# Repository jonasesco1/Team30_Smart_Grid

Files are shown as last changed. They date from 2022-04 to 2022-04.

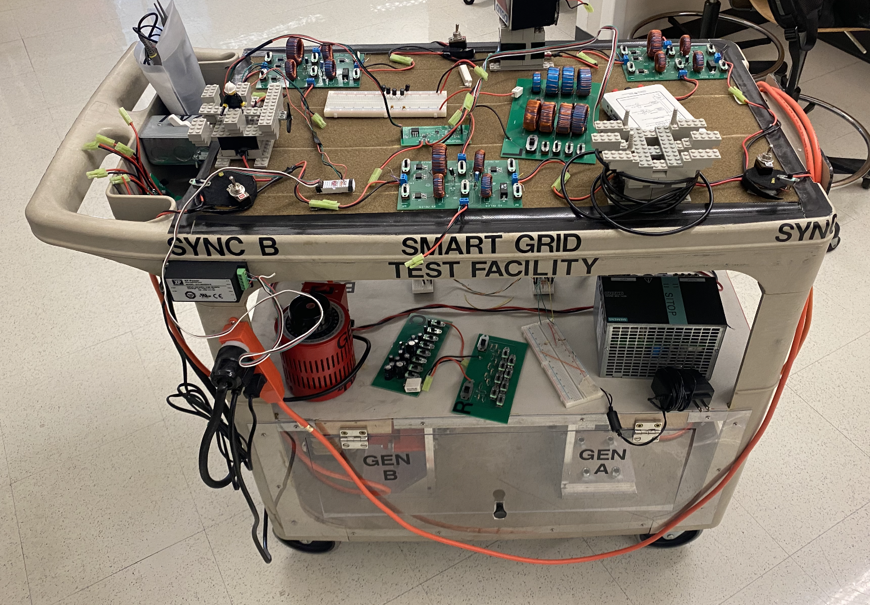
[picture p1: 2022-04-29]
2022 Team/Hardware Documentation/Pictures/Grid Side view.png

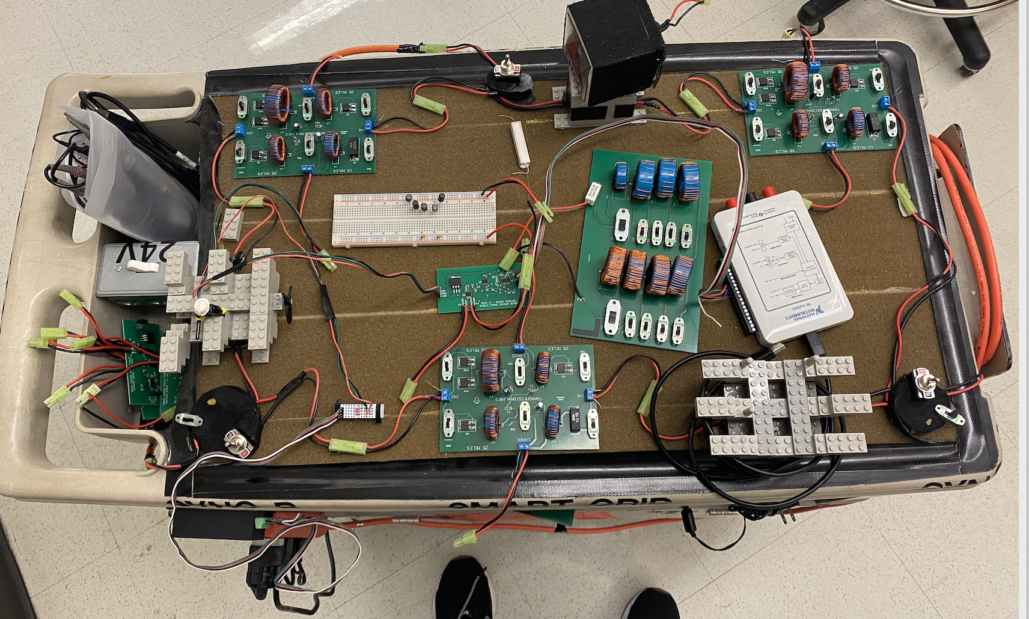
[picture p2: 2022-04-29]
Hardware Documentation/Pictures/Grid Sky View.png

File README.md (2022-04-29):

# Team30 Smart Grid

## The Team

The creators of this project are:

| Name  | Email |
| ------------- | ------------- |
| Jonas Escobar  | jesco@bu.edu  |
| Aidan McCall  | apm22@bu.edu  |

## The Client

The client of this project is Professor Alan Pisano (apisano@bu.edu). 

## The Purpose

The purpose of this project is to design a test facility that can be used by a professor to teach students about how an electrical grid works including generation, transmission, distribution, phasors, and loads. 

## How to use

This repository is meant to help inform a professor, student, or future design team how the test facility works and operates. Please note that there were two groups that worked on this project: Labeled as 2015 Team and 2022 Team. The 2015 Team did a majority of the design on the grid model, and the 2022 Team designed the data acquisition system. Most of the 2015 Team's work carried for over into into the 2022 Team. However, in the event of any differences, default to the 2022 Team. 

Both folders are set up the same way including software documentation, hardware documentation, pictures, and all reports completed throughout the semester. The 2022 hardware documentation and software documentation Readme's and 2022 User's Manual will be the most helpful in operating the test facility. 

### Hardware

Hardware can be split up into two different categories: data acquisition unit hardware and test facility hardware. The DAQ information is found in the 2022 Hardware documentation folder and includes information about the sensor boards, myDAQ, and PicoScope. The test facility hardware is found in the 2015 Hardware documentation folder and includes information about the generators, synchronization method, and transmission line boards. 

### Software

Most of the software documentation is found in the 2022 Software Documentation folder including all MATLAB code for the myDAQ and information on the PicoScope. Code for the MSP430 feedback boards is found in the 2015 Software Documentation folder.

### Reports

All reports for all teams are found the respective folders. The most important report is the User's Manual although the other reports highlight the engineering process each team went through. A user only needs to read the 2022 User's Manual in order to understand and operate the test facility. However, the 2015 User's Manual has good supplemental information in case of modifications or confusion.

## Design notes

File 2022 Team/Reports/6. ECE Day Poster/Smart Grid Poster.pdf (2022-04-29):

# Team 30: Smart Grid

Scale Energy Grid Model | Boston University ECE
Aidan McCall and Jonas Escobar
Background | Software

# Purpose

- The energy grid brings electric power to systems that need it: houses, businesses, manufacturing buildings, etc.
- The grid infrastructure is made up of generation, transmission, and distribution, and then consumption by the end use system
- An important function is to integrate multiple different generation sources into the same transmission grid

Educational Tool
- Create an educational tool that can be used by a professor to teach students about electrical grids by:
- Measuring voltage, current, phase angle, and power factor on a grid under different transmission and load configurations
- Verifying grid measurements using circuit principles learned in class
- Simulating blackouts
Updated Design
- Fix bugs associated with inherited grid model
- Add data acquisition system to enhance the already-functioning grid

Measure
Frequency

Adjust
Frequency

CONSUMPTION
(LOADS)

DATA READOUT

TRANSMISSION

GENERATION

DISTRIBUTION | Picoscope
- Live waveform data
- Verify stable grid
operation
- Synchronize generators

Special Thanks to:
- Power Pooches for designing the original grid model
- Professors Pisano, Osama and Hirsch for guidance and support

Connect hardware
- Connect data acquisition unit at the push of a button Frequency Analysis
- Graph current and voltage waveforms
- Provide frequency analysis to confirm 60 Hz

Visualization
- Graph current and voltage waveforms
- Plot Phasor Diagram to
visualize leading and
lagging power factor
- Provide RMS current, RMS voltage, phase angle, and
power factor data

FEEDBACK

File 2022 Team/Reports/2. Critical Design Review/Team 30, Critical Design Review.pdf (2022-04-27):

# Team 30: Smart Grid

By: Aidan McCall and Jonas Escobar

# Problem Statement

We have a fully functional Electric Grid model from a previous Senior Design

team that has no working method for data collection, so it cannot be properly

utilized by professors for classes like EC 417.

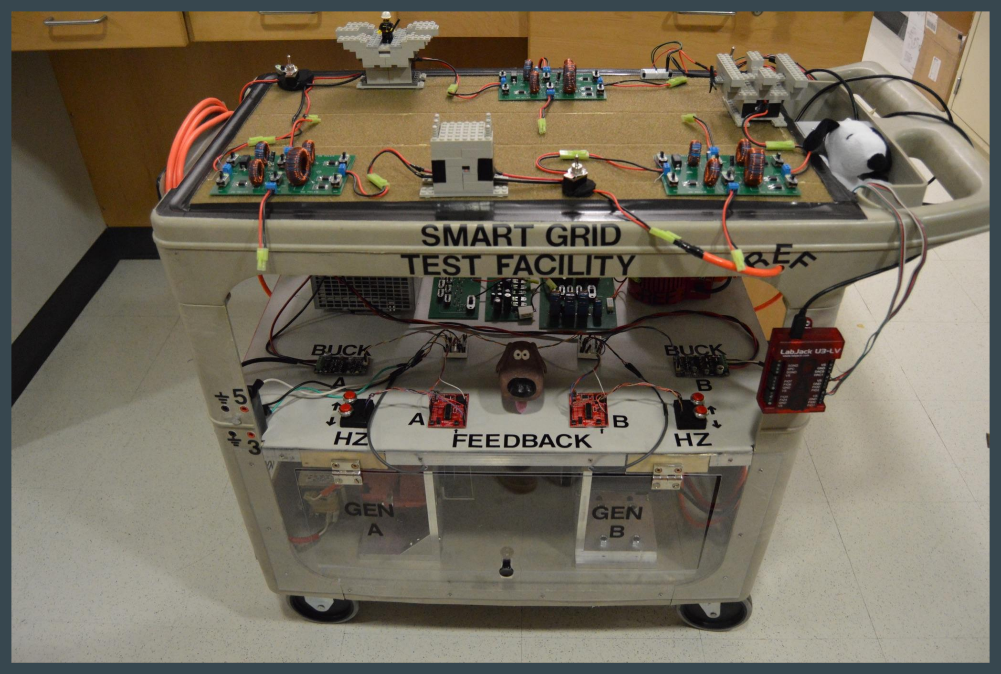
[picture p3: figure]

# The Smart Grid Model

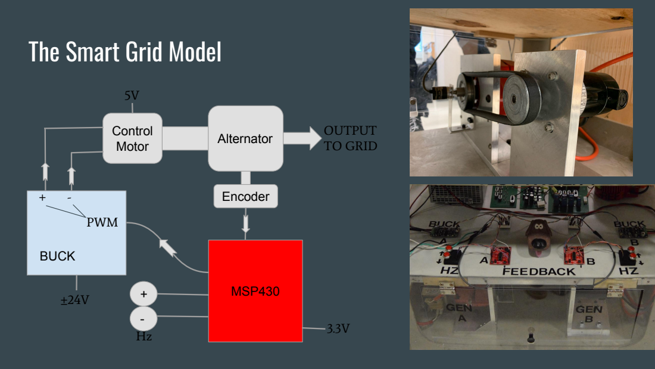
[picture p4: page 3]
MSP430; BUCK; PWM; Control; Motor; Alternator; Encoder; OUTPUT TO GRID

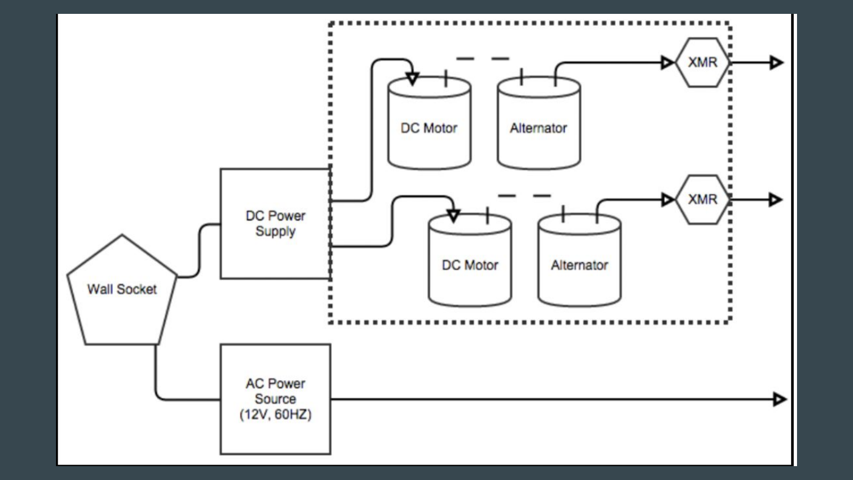
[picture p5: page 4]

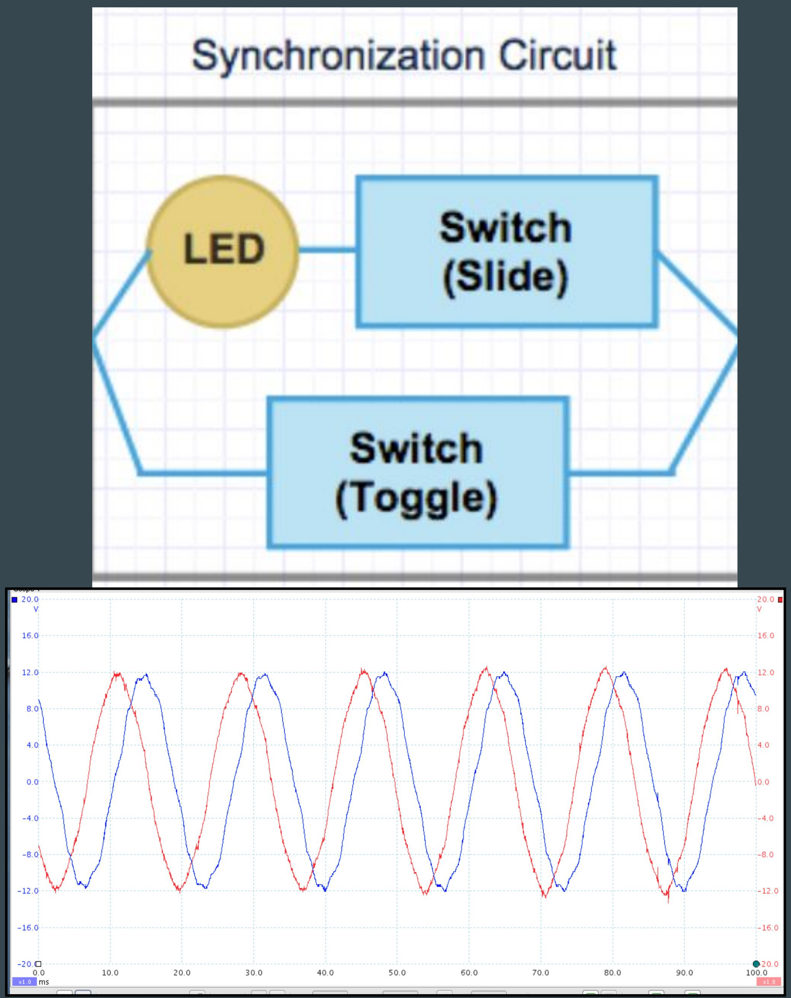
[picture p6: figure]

# Synchronization

- Synchronization
- "Sync Bulb" method
- Problem: LED can be hard to

time and a big oscilloscope

can practically be transported

- Solution: Picoscope

# Data Collection

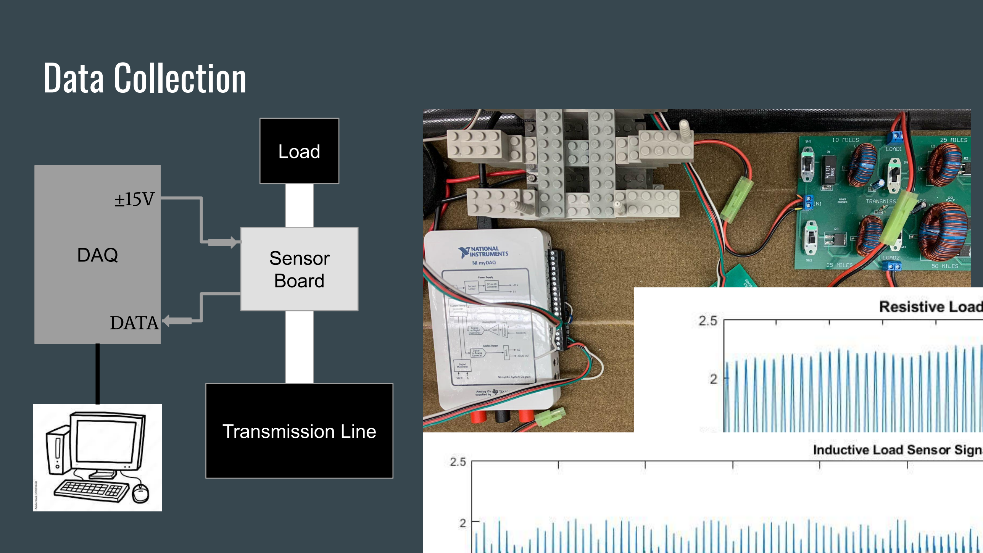
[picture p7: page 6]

Transmission Line

DAQ | Sensor Board Load

±15V

DATA

# GUI

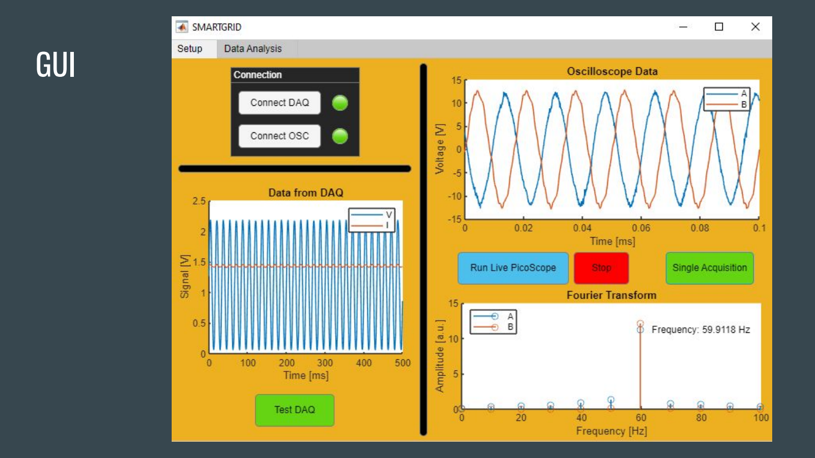
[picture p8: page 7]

# Next Steps

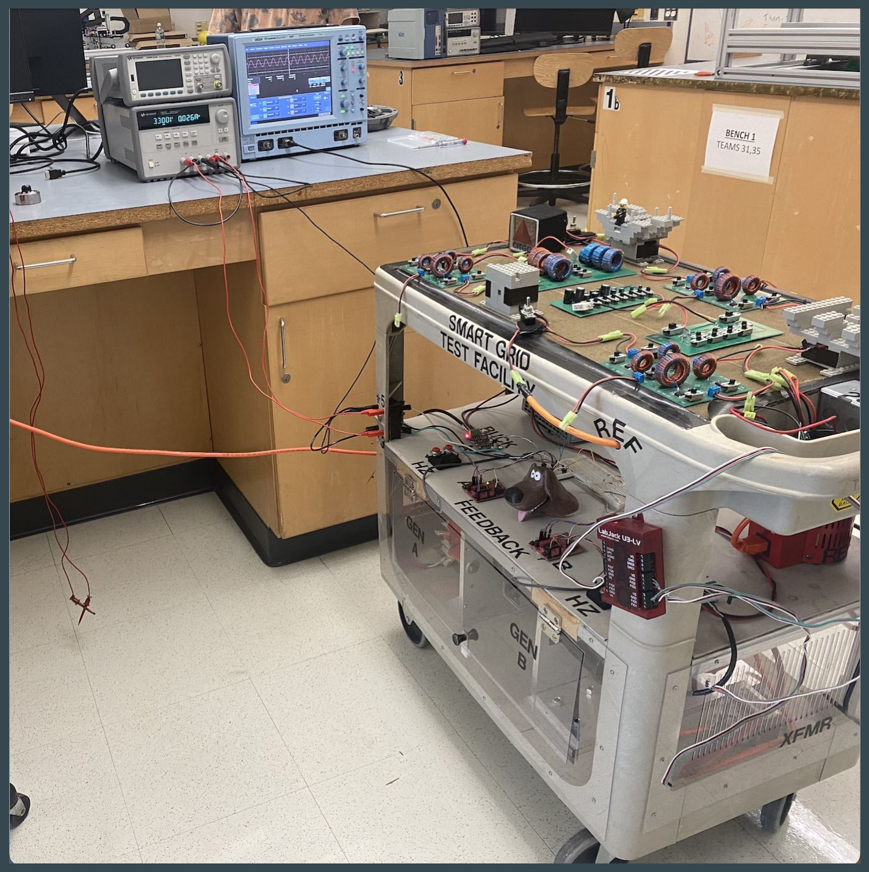
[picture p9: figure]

- Consolidate everything into one movable cart
- Use the DAQ
- Update our GUI and DAQ code to be able to calculate phasors (and therefore power factor)

# Gantt Chart

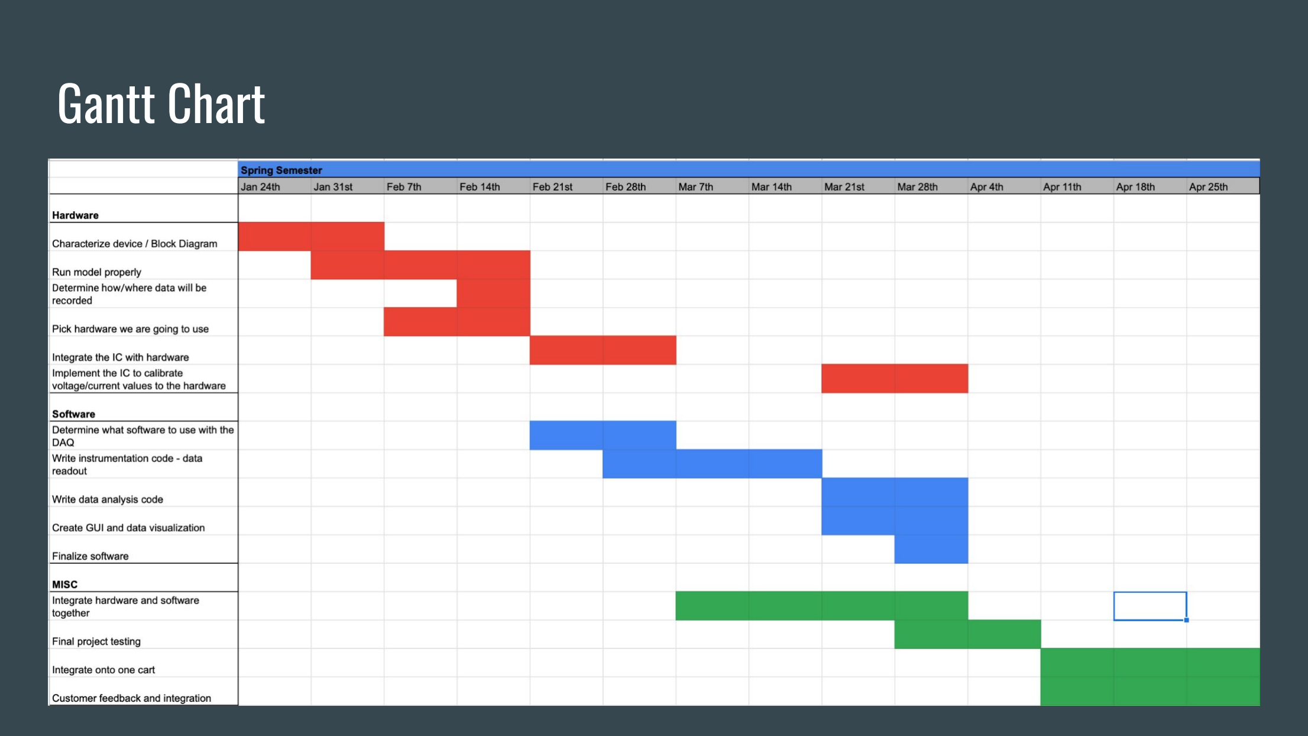
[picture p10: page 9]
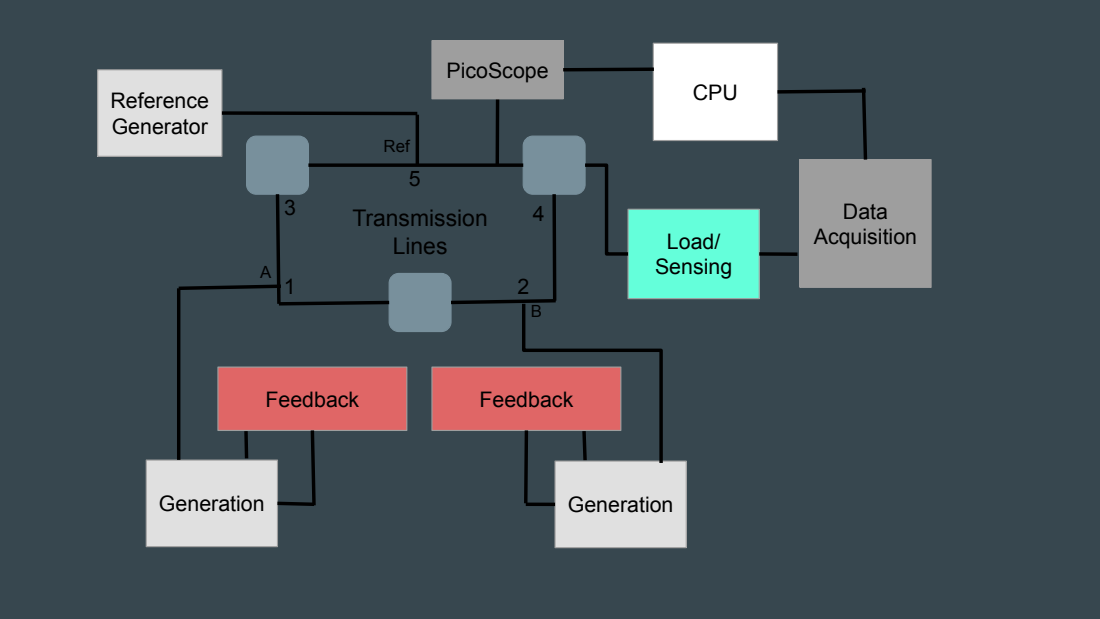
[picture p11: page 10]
Generation; Feedback; Reference Generator; Load/ Sensing; CPU; Data Acquisition; Transmission Lines; PicoScope; Ref

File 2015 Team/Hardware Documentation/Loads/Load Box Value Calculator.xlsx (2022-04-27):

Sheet: Sheet1
L | C | R | X_L | X_C |  | 10-25 Impedance |  |  | 10-50 Impedance
0.0015 | 1.125e-05 | 1000 | 0.565486677646163i | -235.785100876882i |  | Z1 | Z2 | Z3 | Z1 | Z2 | Z3
0.0033 | 2.25e-05 | 2000 | 1.24407069082156i | -117.892550438441i |  | m | 2.8+12.5161051319017i | 3444.91218813625i | m | 5.6+25.0699093756465i | 2009.53210974615i
0.0068 | 4.5e-05 | 4000 | 2.56353960532927i | -58.9462752192205i |  | Parellel Comp (Z3 || Load Box) |  |  | Parellel Comp (Z3 || Load Box)
0.012 | 9e-05 | 8000 | 4.5238934211693i | -29.4731376096102i |  | (C LOAD) | Z_Tot | Ø ANGLE | (C LOAD) | Z_Tot | Ø ANGLE
0.024 | 0.00018 | 16000 | 9.0477868423386i | -14.7365688048051i |  | -253.109006189401i | #NUM! | #NUM! | -267.128135434533i | #NUM! | #NUM!
0.048 | 0.00036 | 32000 | 18.0955736846772i | -7.36828440240256i |  | -122.07005912862i | #NUM! | #NUM! | -125.239961513925i | #NUM! | #NUM!
0.096 | 0.00072 | 64000 | 36.1911473693544i | -3.68414220120128i |  | -59.9724708312212i | #NUM! | #NUM! | -60.7276187011198i | #NUM! | #NUM!
0.192 | 0.00144 | 128000 | 723.822947387088i | -1.84207110060064i |  | -29.7274726534228i | #NUM! | #NUM! | -29.9118446646924i | #NUM! | #NUM!
0.3836 |  |  |  |  |  | -14.7998794000163i | #NUM! | #NUM! | -14.8454353305626i | #NUM! | #NUM!
 |  |  |  |  |  | -7.38407812505893i | #NUM! | #NUM! | -7.39540087226755i | #NUM! | #NUM!
 |  |  |  |  |  | -3.68808640471743i | #NUM! | #NUM! | -3.69090886745828i | #NUM! | #NUM!
 |  |  |  |  |  | -1.84305662393427i | #NUM! | #NUM! | -1.84376121504777i | #NUM! | #NUM!
NOTE: All calculations are done as though f = 60hz |  |  |  |  |  | (L LOAD) |  |  | (L LOAD)
NOTE: In each case, Z1 || Z2 + Z3 is taken to be accurate under assumption of phase locked generation. |  |  |  |  |  | 0.565393867530185i | #NUM! | #NUM! | 0.565327593239927i | #NUM! | #NUM!
10 Mile Transmission Line Structure |  |  |  |  |  | 1.24362157831258i | #NUM! | #NUM! | 1.2433009821395i | #NUM! | #NUM!
Line Stats: |  |  |  |  |  | 2.56163335976669i | #NUM! | #NUM! | 2.56027349056469i | #NUM! | #NUM!
R (ohm) | L (H) | C (F) | Z_RL | Z_C |  | 4.51796039002965i | #NUM! | #NUM! | 4.51373202960227i | #NUM! | #NUM!
1.1 | 0.0133 | 2.2e-07 | m | 12057.1926584769i |  | 9.0240858014066i | #NUM! | #NUM! | 9.00723236793667i | #NUM! | #NUM!
 |  |  |  |  |  | 18.0010172154172i | #NUM! | #NUM! | 17.9340796443001i | #NUM! | #NUM!
25 Mile Transmission Line Structure |  |  |  |  |  | 35.8148875971865i | #NUM! | #NUM! | 35.5508852305952i | #NUM! | #NUM!
Line Stats: |  |  |  |  |  | 598.144619997175i | #NUM! | #NUM! | 532.14654669525i | #NUM! | #NUM!
R (ohm) | L (H) | C (F) | Z_RL | Z_C |  | (R LOAD) |  |  | (R LOAD)
2.8 | 0.0332 | 5.5e-07 | 2.8+12.5161051319017i | 4822.87706339077i |  | 922.284342840616+267.723614557382i | #NUM! | #NUM! | 801.517174931232+398.857610208817i | #NUM! | #NUM!
 |  |  |  |  |  | 1495.82225666919+868.424026493665i | #NUM! | #NUM! | 1004.75469736193+999.988696362612i | #NUM! | #NUM!
50 Mile Transmission Line Structure |  |  |  |  |  | 1703.4113657879+1977.88654428311i | #NUM! | #NUM! | 806.103424585337+1604.55943087601i | #NUM! | #NUM!
Line Stats: |  |  |  |  |  | 1251.38511223681+2906.04820998664i | #NUM! | #NUM! | 474.8177529208+1890.26191964967i | #NUM! | #NUM!
R (ohm) | L (H) | C (F) | Z_RL | Z_C |  | 708.853356465964+3292.29109018057i | #NUM! | #NUM! | 248.469278768007+1978.32542262304i | #NUM! | #NUM!
5.6 | 0.0665 | 1.1e-06 | 5.6+25.0699093756465i | 2411.43853169538i |  | 366.608150966759+3405.44553540077i | #NUM! | #NUM! | 125.698651253649+2001.63850112596i | #NUM! | #NUM!
 |  |  |  |  |  | 184.892743928192+3434.9600120885i | #NUM! | #NUM! | 63.0350307443161+2007.55287664741i | #NUM! | #NUM!
 |  |  |  |  |  | 92.6471115579199+3442.41874154405i | #NUM! | #NUM! | 31.540814312+2009.03693569046i | #NUM! | #NUM!
 |  |  |  |  |  | 25-25 Impedance |  |  | 25-50 Impedance
 |  |  |  |  |  | Z1 | Z2 | Z3 | Z1 | Z2 | Z3
 |  | 293 | 80.71 | -89.05 | 88.2 | 2.8+12.5161051319017i | 2.8+12.5161051319017i | 2411.43853169539i | 2.8+12.5161051319017i | 5.6+25.0699093756465i | 1607.62568779693i
 |  | 357 | 75 | -89.2 | 88.5 | Parellel Comp (Z3 || Load Box) |  |  | Parellel Comp (Z3 || Load Box)
 |  |  |  |  |  | (C LOAD) | Z_Tot | Ø ANGLE | (C LOAD) | Z_Tot | Ø ANGLE
 |  |  |  |  |  | -261.338165996544i | 5.6-236.305955732741i | -88.642 | -276.310665090095i | 8.4-238.724650582547i | -87.985
 |  |  |  |  |  | -123.952447890884i | 5.6-98.9202376270806i | -86.760 | -127.22217673213i | 8.4-89.6361622245818i | -84.646
 |  |  |  |  |  | -60.4232889490869i | 5.6-35.3910786852835i | -81.009 | -61.1899050718552i | 8.4-23.603890564307i | -70.411
 |  |  |  |  |  | -29.8378221019676i | 5.6-4.8056118381642i | -40.634 | -30.0235697211649i | 8.4+7.5624447863833i | 41.996
#NUM! |  |  |  |  |  | -14.8271793452483i | 5.6+10.2050309185551i | 61.244 | -14.8729037559009i | 8.4+22.7131107516473i | 69.704
#NUM! |  |  |  |  |  | -7.39086760898557i | 5.6+17.6413426548178i | 72.389 | -7.40221120375308i | 8.4+30.1838033037951i | 74.448
#NUM! |  |  |  |  |  | -3.68977936411868i | 5.6+21.3424308996847i | 75.298 | -3.692604419663i | 8.4+33.8934100878852i | 76.081
#NUM! |  |  |  |  |  | -1.84347931396547i | 5.6+23.1887309498379i | 76.423 | -1.8441842283623i | 8.4+35.7418302791859i | 76.774
#NUM! |  |  |  |  |  | (L LOAD) |  |  | (L LOAD)
 |  |  |  |  |  | 0.565354101091498i | 5.6+25.5975643648949i | 77.660 | 0.565287836123045i | 8.4+38.1513023436712i | 77.583
 |  |  |  |  |  | 1.24342920077134i | 5.6+26.2756394645747i | 77.969 | 1.24310870376475i | 8.4+38.8291232113129i | 77.793
 |  |  |  |  |  | 2.56081726495259i | 5.6+27.593027528756i | 78.528 | 2.55945826184724i | 8.4+40.1454727693954i | 78.182
 |  |  |  |  |  | 4.51542242365983i | 5.6+29.5476326874632i | 79.268 | 4.51119881024452i | 8.4+42.0972133177927i | 78.716
 |  |  |  |  |  | 9.01396618154105i | 5.6+34.0461764453445i | 80.659 | 8.99715049057766i | 8.4+46.5831649981259i | 79.778
 |  |  |  |  |  | 17.9607948452888i | 5.6+42.9930051090922i | 82.579 | 17.8941555235595i | 8.4+55.4801700311077i | 81.390
 |  |  |  |  |  | 35.6560177461466i | 5.6+60.68822800995i | 84.728 | 35.3943437840099i | 8.4+72.9803582915581i | 83.434
 |  |  |  |  |  | 556.717376556851i | 5.6+581.749586820654i | 89.448 | 499.104439221122i | 8.4+536.69045372867i | 89.103
 |  |  |  |  |  | (R LOAD) |  |  | (R LOAD)
 |  |  |  |  |  | 853.265627577104+353.840919584712i | 858.865627577104+378.873129848515i | 23.804 | 721.017977106644+448.49866643691i | 729.417977106644+486.084680944458i | 33.680
 |  |  |  |  |  | 1184.9240115454+982.75282240956i | 1190.5240115454+1007.78503267336i | 40.248 | 785.018122632995+976.618038131468i | 793.418122632995+1014.20405263902i | 51.964
 |  |  |  |  |  | 1066.24363994654+1768.64328230983i | 1071.84363994654+1793.67549257363i | 59.139 | 556.262663129187+1384.06015119473i | 564.662663129187+1421.64616570228i | 68.338
 |  |  |  |  |  | 666.336209805333+2210.58493027183i | 671.936209805333+2235.61714053563i | 73.271 | 310.518140526993+1545.22607039216i | 318.918140526993+1582.81208489971i | 78.608
 |  |  |  |  |  | 355.367568531046+2357.87934121597i | 360.967568531046+2382.91155147977i | 81.386 | 159.914348978019+1591.55803684291i | 168.314348978019+1629.14405135046i | 84.101
 |  |  |  |  |  | 180.693754588183+2397.82191037506i | 186.293754588183+2422.85412063886i | 85.603 | 80.5610589874924+1603.57843692617i | 88.9610589874924+1641.16445143372i | 86.897
 |  |  |  |  |  | 90.7311245021612+2408.01989841963i | 96.3311245021612+2433.05210868343i | 87.733 | 40.3567290444282+1606.6119610112i | 48.7567290444282+1644.19797551875i | 88.301
 |  |  |  |  |  | 45.4138487694418+2410.58296368918i | 51.0138487694418+2435.61517395298i | 88.800 | 20.1879119998845+1607.37213618823i | 28.5879119998845+1644.95815069578i | 89.004
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

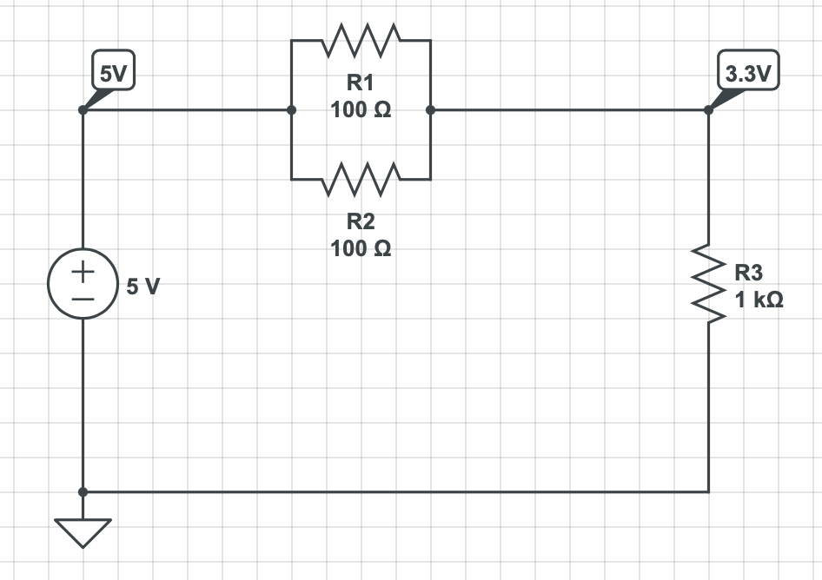
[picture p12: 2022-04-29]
2022 Team/Hardware Documentation/Pictures/Voltage Divider Schematic.png

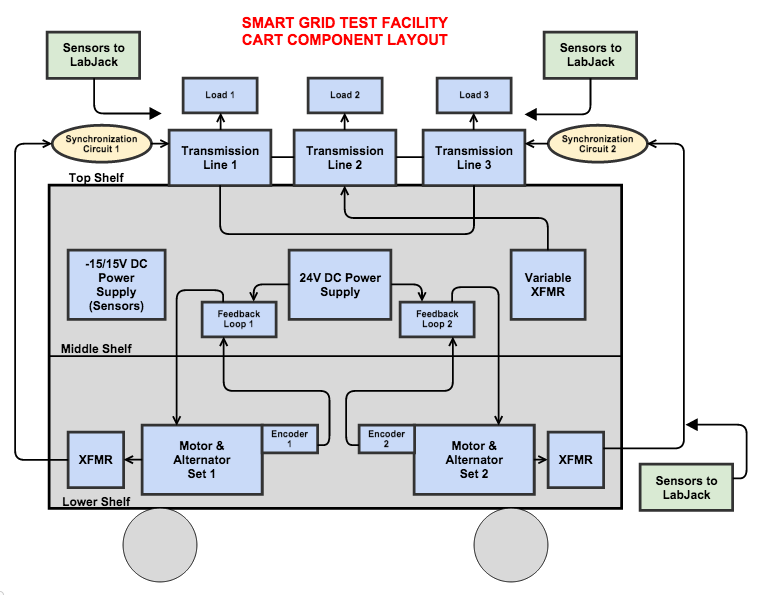
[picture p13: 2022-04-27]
2015 Team/Reports and Specifications/9. Misc./Cart Layout.png

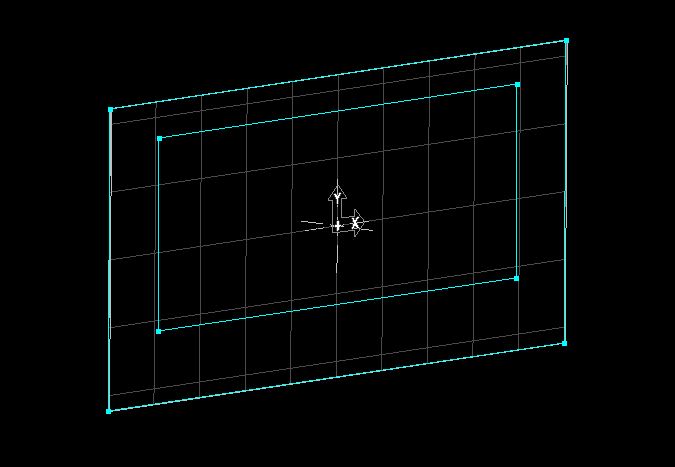
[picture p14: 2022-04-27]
2015 Team/Hardware Documentation/Safety Enclosure/SidePanels.JPG

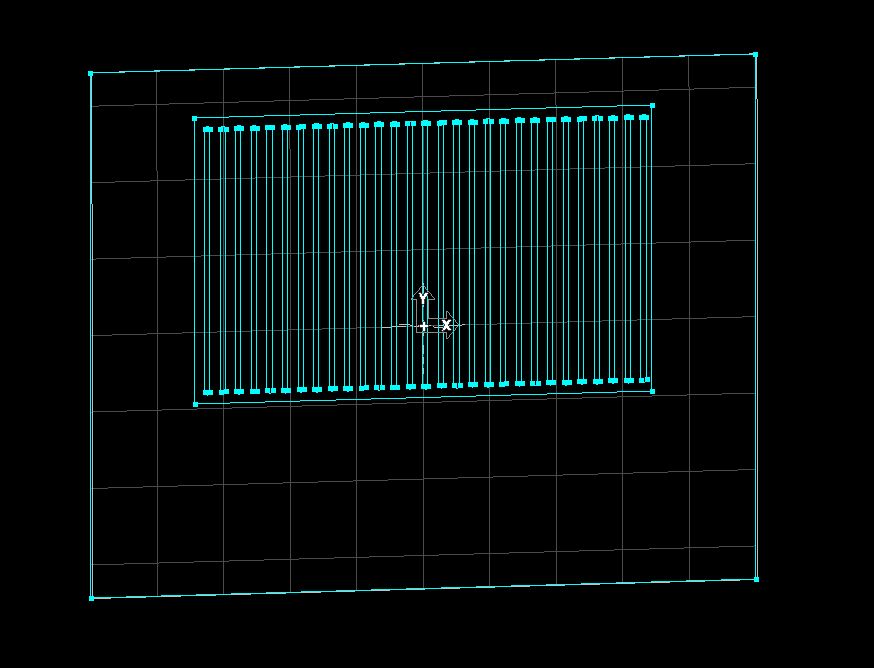
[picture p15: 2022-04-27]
2015 Team/Hardware Documentation/Safety Enclosure/FrontBackPanels.JPG

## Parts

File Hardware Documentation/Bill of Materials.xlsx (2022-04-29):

Part Name | Quantity | Description | Unit Cost | Source | Notes
NI myDAQ | 1 | Data Acquisition Unit | $416 | https://www.ni.com/en-us/shop/hardware/products/mydaq-student-data-acquisition-device.html | Given to us by professor (cost us $0) Comes with USB-B Cable
Picoscope Series 2204A | 1 | Used to monitor grid | $149 | https://www.newark.com/search?st=picoscope%202204a | Student owned picoscope used (cost us $0) Comes with USB-B Cable
ECL30UD02-S: AC/DC Power supply (+/- 15 V) | 1 | Used to power sensor boards | $89.62 | https://www.mouser.com/ProductDetail/XP-Power/ECL30UD02-S?qs=w%2Fv1CP2dgqozyucSuuKavA%3D%3D
Resistors 0.5W 5% Tolerance | 3 | 1000 Ohm (1x), 100 Ohm (2x) | $5 |  | Used in Voltage Divider to power the feedback circuits
Smart Grid Test Facility | 1 | Inherited from previous Senior Design Team | $1906.57 | N/A | See their User's Manual for more information

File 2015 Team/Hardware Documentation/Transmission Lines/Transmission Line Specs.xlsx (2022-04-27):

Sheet: Final Specs
TRANSMISSION LINE CHARACTERISTICS
R (Ω/mi) | L (mH/mi) | C (nF/mi)
0.1128 | 1.329 | 22
FINAL TRANSMISSION LINE SPECS |  |  |  |  |  |  |  |  |  | NOTES
TL No. | Length (mi) | R (Ω) | L (mH) | C (nF)
1 | 10 | 1.1 | 13.3 | 220
2 | 25 | 2.8 | 33.2 | 550
3 | 25 | 2.8 | 33.2 | 550
4 | 50 | 5.6 | 66.5 | 1100
RESISTORS
TL No. | Part No. | Resistance (Ω) | Power Rating (W @ 2A) | Quantity/PCB | Extras | Quantity Total | $/item | Total $ | In Cart?
1 | SM8035FT1R00CT-ND | 1 | 4 | 1 | 1 | 4 | 1.44 | 5.76 | Y
2 | PWR163S-25-3R00J-ND | 3 | 12 | 2 | 1 | 7 | 2.64 | 18.48 | Y
4 | PWR163S-25-3R00J-ND | 6 | 24 | 2 | 0 | 6 | 2.64 | 15.84 | Y | 2 in series per PCB
INDUCTORS
TL No. | Part No. | Inductance (mH) | Current Rating (A) | Quantity/PCB | Extras | Quantity Total | $/item | Total $ | In Cart? | winding our own
1 | Winding Our Own | 13 | 2 | 1 | 0 | 3 |  | 0
2 | Winding Our Own | 33 | 2 | 2 | 0 | 6 |  | 0
4 | Winding Our Own | 67 | 2 | 1 | 0 | 4 |  | 0
CAPACITORS
TL No. | Part No. | Capacitance (uF) | Voltage Rating (V) | Quantity/PCB | Extras | Quantity Total | $/item | Total $ | In Cart?
1 | 445-1318-1-ND | 0.22 | 16 | 1 | 3 | 6 | 0.1 | 0.6 | Y | http://www.digikey.com/product-detail/en/C1608X7R1C224K080AC/445-1318-1-ND/567690
2 | 490-5892-1-ND | 0.55 | 16 | 2 | 3 | 9 | 0.32 | 2.88 | Y | http://www.digikey.com/product-detail/en/GRM219R71C564KA01D/490-5892-1-ND/3482899
4 | 399-5090-1-ND | 1.1 | 16 | 1 | 3 | 6 | 0.11 | 0.66 | Y | http://www.digikey.com/product-detail/en/C0603C105K4PACTU/399-5090-1-ND/1465624
TERMINAL BLOCKS
TB No. | Part No. | Terminals | Current Rating (A) | Quantity/PCB | Extras | Quantity Total | $/item | Total $ | In Cart?
ALL | https://www.sparkfun.com/products/8432 | 2 | 2 | 4 | 0 | 12 | 0.95 | 11.4 | Y - other | 5mm pitch
SWITCHES
Switch No. | Part No. | Terminals | Current Rating (A) | Quantity/PCB | Extras | Quantity Total | $/item | Total $ | In Cart?
ALL | CWI334-ND | 2 | 2 | 6 | 4 | 22 | 0.6 | 13.2 | Y
PURCHASE ORDER SUMMARY
Type | Quantity | Cost
R | 17 | 40.08
L | 13 | 0
C | 21 | 4.14
TB | 12 | 11.4
S | 22 | 13.2
Total: | 85 | 68.82
Digikey |  | 57.42
Sparkfun |  | 11.4

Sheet: Inductor Winding
N TURNS CALCULATOR
No. | Toroid | Wire AWG | R-avg (mm) | L (mH) | A-cross | u | N (# turns) | Max
1 - 10mi | T38, TDK | 22 | 10.025 | 13.3 | 5.25e-05 | 0.01256636 | 35.63 | 72.1
2&3 - 25 mi | T38, TDK | 22 | 10.025 | 33.2 | 5.25e-05 | 0.01256636 | 56.3 | 72.1 | 495-3861-ND (http://www.digikey.com/scripts/DkSearch/dksus.dll?Detail&itemSeq=167604490&uq=635609278339648752&CSRT=16876739212055281624)
4 - 50 mi | N30, TDK | 22 | 14.75 | 66.5 | 9.75e-05 | 0.01256636 | 70.92 | 112 | 495-3868-ND (http://www.digikey.com/scripts/DkSearch/dksus.dll?Detail&itemSeq=167604242&uq=635609270430861844&CSRT=16876739212055281624)
Max Turns Per Toroid
Wire Size | D Toroid (mm) | D Wire | Nmax
18 | 14.8 | 1.02362 | 45.42264903
22 | 23 | 0.64516 | 111.9979075
22 | 20.5 | 0.64516 | 99.8242219
MEASURED VALUES OF SELF-WOUND INDUCTORS (mH)
T-Line | L - 10mi | L - 25mi (top) | L - 25mi | L - 50 mi
1 | 13.12 | 27.2 | 34.3
2
3

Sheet: Synch Testing
Generator Alone |  |  | Generator + Wall Adapter
Load (Ω) | Alternator Output Current (mA) | Outcome | Load (Ω) | Generator Output Current (A) | Wall Adapter Output Current (A)
10000 | 1 | ~60Hz signal | 1000 | 1 | 1.2
1000 | 10 | ~60Hz signal | 560 | 1.4 | 1.8
100 | 70 | Frequency drops by ~5% | 330 | 1.4 | 1.8
51 | 100 | Frequency drops by ~10% | 270 | 1.6 | 1.85
21 | 700 | Resistor melts | 150 | 1.3 | 1.5
10 | 900 | Frequency drops by ~20% | 100 | 1.4 | 1.6

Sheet: MSP430 Testing-Raw
MSP430 Testing Data |  |  |  |  |  | MSP430 Testing Data
Input Signal (from Encoder) |  | Output Signal (by MSP430) |  |  |  | Input Signal (from Encoder) |  | Output Signal (by MSP430)
Frequency (kHz) | Alternator Frequency | Frequency (kHz) | Duty Cycle (%) (Instantaneous) | Factor |  | Frequency (kHz) | Alternator Frequency | Frequency (kHz) | Duty Cycle (%) (Instantaneous)
1.8 | 61.25 | 50 | 50 | 29.3877551 |  | 1.7 | 60 | 49.88 | 49.9
2 | 72 | 49.8 | 42 | 27.77777778 |  | 1.72 | 59.7 | 49.75 | 51
2.03 | 70.7 | 49.8 | 45 | 28.71287129 |  | 1.72 | 60.1 | 49.75 | 50
1.92 | 66.8 | 49.8 | 48 | 28.74251497 |  | 1.8 | 61.25 | 50 | 50
1.9 | 66.9 | 49.75 | 48.5 | 28.40059791 |  | 1.83 | 65.2 | 49.75 | 49.8
1.72 | 59.7 | 49.75 | 51 | 28.81072027 |  | 1.9 | 66.9 | 49.75 | 48.5
1.72 | 60.1 | 49.75 | 50 | 28.61896839 |  | 1.92 | 66.8 | 49.8 | 48
1.83 | 65.2 | 49.75 | 49.8 | 28.06748466 |  | 2 | 72 | 49.8 | 42
1.7 | 60 | 49.88 | 49.9 | 28.33333333 |  | 2.03 | 70.7 | 49.8 | 45
 |  |  |  | 28.53911374 | avg
add bracket
1.72 | 59.4 | 49.75 | 50

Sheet: Alternator Testing
Alternator Measurements | Alternator 1 |  | Alternator 2 |  | Transmission Line Configurations
 | 15V Input | 16.5V Input | 15V Input | 16.5V Input | Load Point 1 | Load Point 2 | Switches ON | Miles Simulated
Frequency (Hz) | 61.4 | 66.4 | 65 | 71 | A | B | 1, 6, 5 | 35
Voltage (V) | 17.7 | 19.15 | 17.65 | 19 | C | D | 2, 3, 4 | 75
 |  |  |  |  | A | D | 1, 3, 4 | 60
 |  |  |  |  | C | B | 2, 6, 5 | 50

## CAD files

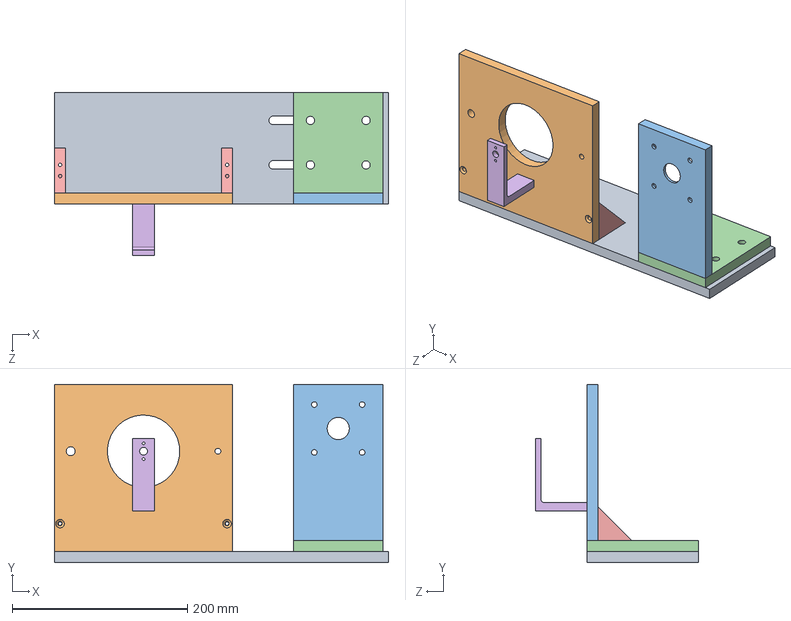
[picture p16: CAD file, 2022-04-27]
2015 Team/Hardware Documentation/Mounting Brackets/MountAssembly.SLDASM
381.0 x 203.2 x 185.8 mm
ECESeniors_Baseplate
ECESeniors_ACBracket1
ECESeniors_DCMotorMount1
ECESeniors_DCMotorMount2
ECESeniors_Gusset x 2
ECESeniors_EncoderMount

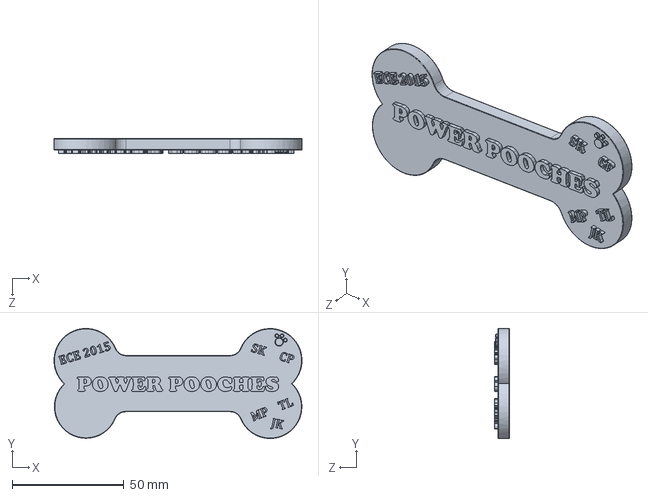
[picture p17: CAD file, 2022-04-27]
2015 Team/Hardware Documentation/Dog Bone/SD_DogBone_Rev1.SLDPRT
110.9 x 49.2 x 6.60 mm

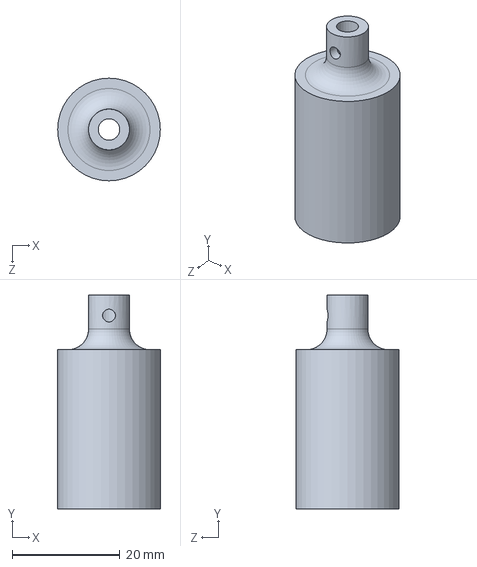
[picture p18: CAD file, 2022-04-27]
2015 Team/Hardware Documentation/Mounting Brackets/ACPulley.SLDPRT
19.1 x 39.8 x 19.1 mm

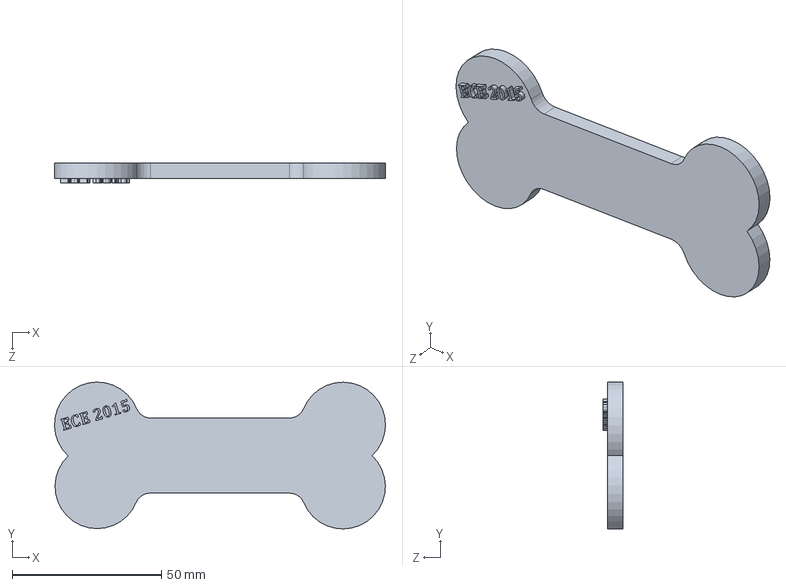
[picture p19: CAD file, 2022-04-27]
2015 Team/Hardware Documentation/Dog Bone/SD_DogBone.SLDPRT
110.9 x 49.2 x 6.60 mm

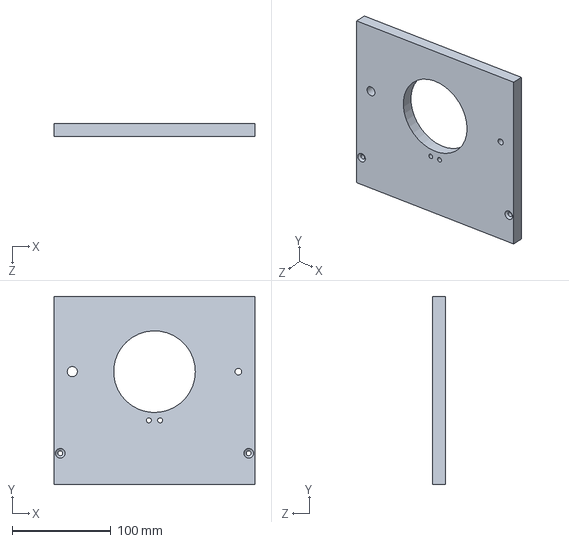
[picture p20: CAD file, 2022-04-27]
2015 Team/Hardware Documentation/Mounting Brackets/ACMount.SLDPRT
203.2 x 190.5 x 12.7 mm

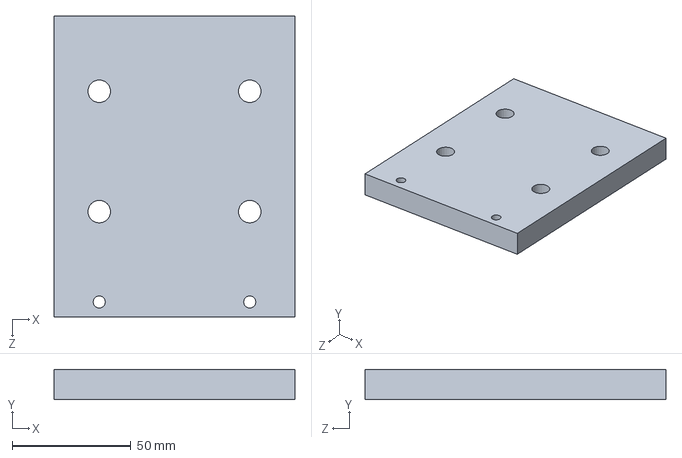
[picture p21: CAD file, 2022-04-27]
2015 Team/Hardware Documentation/Mounting Brackets/DCMount2.SLDPRT
101.6 x 12.7 x 127.0 mm

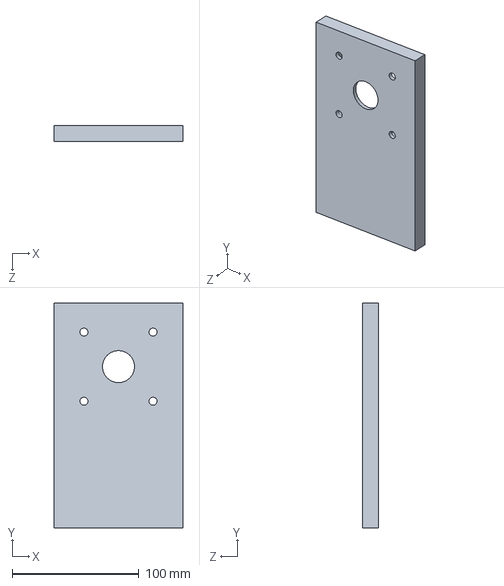
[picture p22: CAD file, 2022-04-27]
2015 Team/Hardware Documentation/Mounting Brackets/DCMount1.SLDPRT
101.6 x 177.8 x 12.7 mm

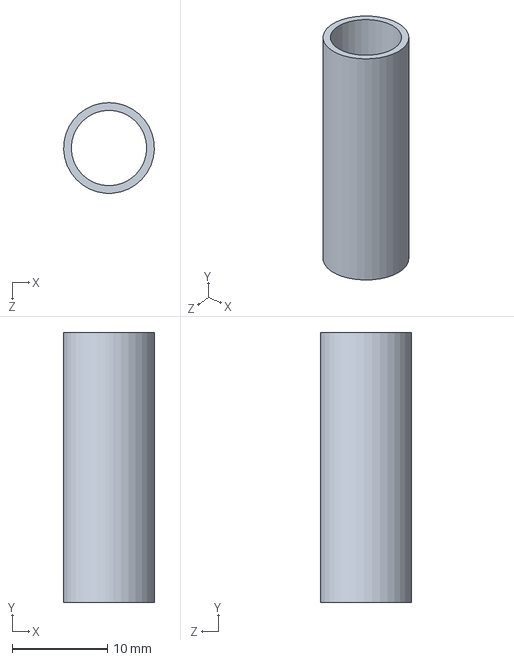
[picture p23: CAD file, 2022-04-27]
2015 Team/Hardware Documentation/Mounting Brackets/DCPulley.SLDPRT
9.54 x 28.4 x 9.55 mm

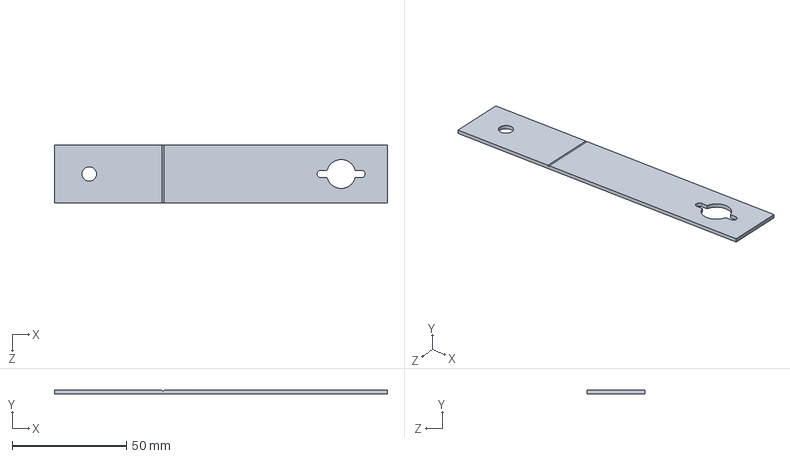
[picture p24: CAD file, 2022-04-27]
2015 Team/Hardware Documentation/Mounting Brackets/EncoderMount2.SLDPRT
146.1 x 1.59 x 25.4 mm

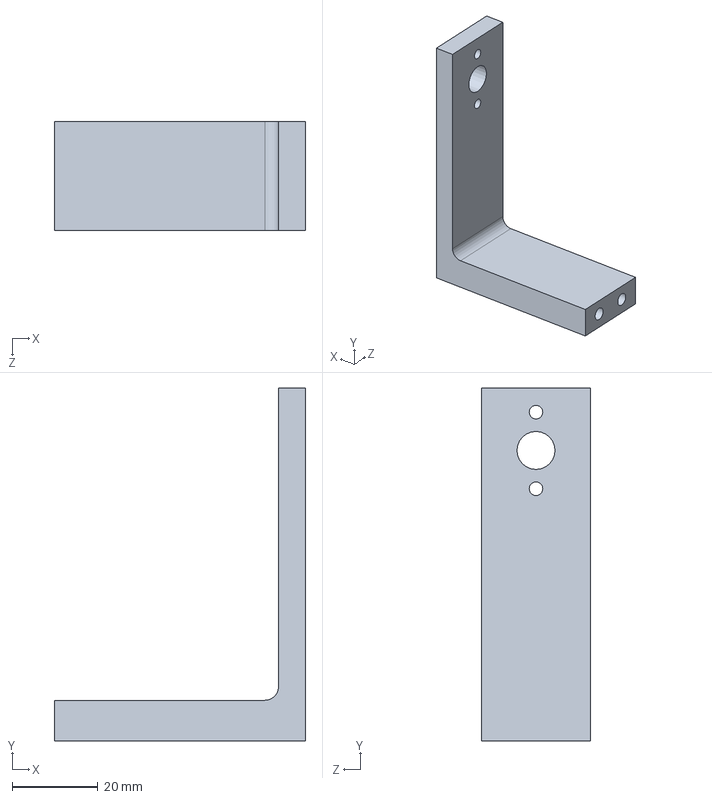
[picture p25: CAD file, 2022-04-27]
2015 Team/Hardware Documentation/Mounting Brackets/EncoderMount.SLDPRT
58.8 x 82.6 x 25.4 mm

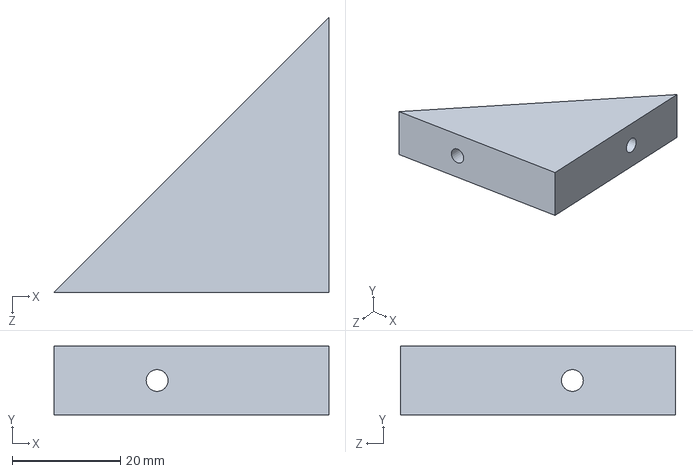
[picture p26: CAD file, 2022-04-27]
2015 Team/Hardware Documentation/Mounting Brackets/Gusset.SLDPRT
50.8 x 12.7 x 50.8 mm

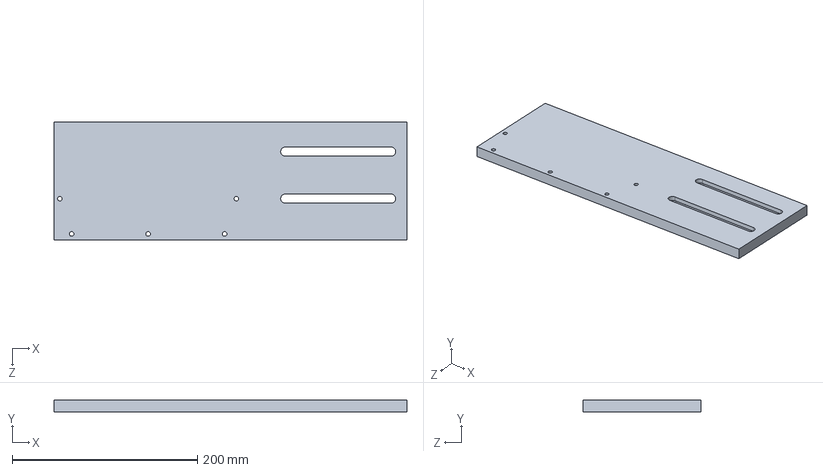
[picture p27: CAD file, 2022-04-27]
2015 Team/Hardware Documentation/Mounting Brackets/Baseplate.SLDPRT
381.0 x 12.7 x 127.0 mm

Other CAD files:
2015 Team/Hardware Documentation/Dog Bone/SD_DogBone_Rev1.STL

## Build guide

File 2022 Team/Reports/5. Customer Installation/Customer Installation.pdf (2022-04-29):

To: | Professor Pisano
From: | Aidan McCall, Jonas Escobar
Team: | Smart Grid (30)
Date: | 04/29/22

Subject: Customer Installation

### 1.0 Introduction

Formal customer installation took place on April 27th with Professor Pisano in the Senior Design lab. However, because of the course format, customer installation involved meetings with Professor PIsano throughout the semester with prototype testing. This formal meeting focused on discussing how to start the test facility, things to watch out for especially in regards to safety, and answering any questions.

### 2.0 Requirements

1. Setup within 10-15 minutes
a. Original
2. Data acquisition unit (DAQ) able to be attached to different points on the grid
a. Original
3. Whole system is able to fit on the given cart (excluding computer) without the need for added benchtop power supplies or oscilloscopes to allow for easy transportation.
a. Original
4. GUI visually demonstrates different aspects of the system including RMS voltage, RMS current, waveforms, phase angle with phasor diagram, and power factor.
a. Original
5. Waveforms are not distorted and maintain a roughly sinusoidal shape
a. Final Product, updated and met after Final Prototype Testing

### 3.0 Assessment and Customer Acceptance

1

Overall, the product installation testing was a success and all requirements were met. The professor, during final prototypes testing and customer installation, witnessed the safe operation of the grid, and how each individual requirement was met.

1. The meeting only took about 10-15 minutes and included setup and operation of the grid with questions from the professor.
2. We showed Professor Pisano the process for connecting the DAQ to different points on the grid.
3. The whole system fit on one cart and only required plugging in two plugs into the wall with no other setup required.
4. Professor Pisano viewed the GUI and was particularly pleased with the phasor diagram.
5. Updated from Final Prototype Testing, the grid is able to maintain a relatively smooth sinusoidal waveform even when different loads are plugged in.

Furthermore, the Professor was able to ask questions and see how he could easily use the test facility without much extra work to run the test facility by himself in a classroom setting. Overall, he verbally accepted the project and declared our project a success (no email or letter because he is in charge of the course).

2

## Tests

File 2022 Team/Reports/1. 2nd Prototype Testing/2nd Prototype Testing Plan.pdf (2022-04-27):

# Memo

To: | Professor Pisano
From: | Aidan McCall, Jonas Escobar
Team: | Team 30: Smart Grid
Date: | 3/4/22

Subject: 2nd Prototype Testing Plan

### 1.0 Materials Required

Hardware
- Smart Grid Test Facility
- DC Power Supply (3.3V, 5V)
- Oscilloscope
- Picoscope
- NI myDAQ
- Banana cables/BNC-Alligator probes

Software
- MATLAB
- MATLAB Signal Processing packages
- Proper daq driver softwares
- NI DAQmx Elvis/driver software
- MATLAB Data Acquisition Toolbox
- MATLAB Data Acquisition Toolbox Support Package for NI-DAQmx Devices
- Data collection scripts

### 2.0 Setup

2.1 Preparing the model for operation

1. Plug the power strip into the wall. Though the presence of a benchtop power supply is a current design flaw (we would like to find a solution for easier transport), we are still using it to power the control boards (MSP430s) for now.
2. Before connecting the model, the 6V output is set to 3.3V, and the +25V output is set to 5V, and both sides are grounded. With the output turned off, we wire the leads to the corresponding inputs on the outside of the model.
3. Turn on the oscilloscope and wire the leads to points 1 and 3, according to Figure 1.

## Senior Design

## ENG EC 464

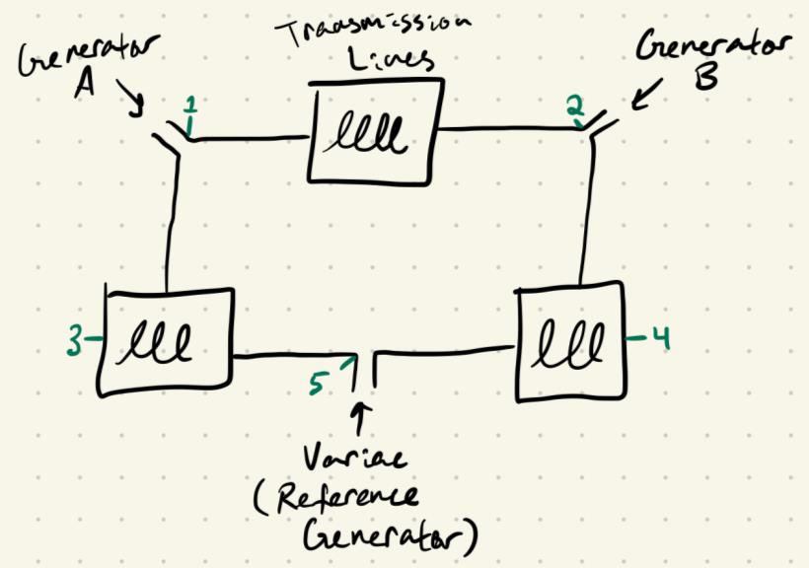
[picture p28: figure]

Figure 1: Basic schematic of the grid

4. All the hardware is set, so turn on the output of the benchtop power supply, in order to let the microcontrollers settle.
5. Then turn on the main switch on top, labeled 24V, to bring power to the rest of the model
6. The variac/reference generator is turned on after. The reference waveform should be visible on the oscilloscope (from point 3), at 60Hz and 24Vpp.

2.2 Setting up the Picoscope

1. Plug the picoscope into a computer.
2. Attach the probes to point 2 (Channel A) and point 4 (Channel B).
3. Pulling up the PicoScope 6 application should bring up a live feed with the 60 Hz, 24Vpp wave being visible on the computer.

2.3 Activating the generators and synchronizing

1. To turn on a generator, we reset the microcontroller by pressing the button labeled by an arrow for the MSP430 corresponding to that generator. When the button for A is pressed, the generator will begin its rotation and it should now be visible on the oscilloscope (from point 1). Their peak-to-peak voltage should be close to the same.
2. Next, flip the slide switch on the synchronization circuit for A to the green/on position, which will give additional feedback via the LED. The LED will flicker on and off due to the phase differences between the reference generator and the signal produced by generator A; the two signals are in phase when the LED is dim, and out of phase when it is lit up (i.e. out of phase means there will be a voltage difference across the diode causing it to be lit).
3. The toggle switch (with on/off labels) should be closed (switched to on) at a moment when the two waves are in phase.
4. Closing this will short circuit the two nodes we’re measuring on the oscilloscope, so the probe at point 3 should be moved to point 5 to compare generator A to the reference. This way we can check that the peak-to-peak voltage is remaining constant, and if it’s not then the main 24V switch should be switched off, along with the variac, to reset the model and start over. In theory, the frequency of generator A should also stabilize to 60Hz, but we’re not currently seeing this behavior.
5. These steps will be repeated for generator B, using the PicoScope to view the waveforms. After closing the toggle switch, generator B should then be compared to either generator A or the reference generator. If voltages are remaining constant, then the grid is running properly. We plan to measure A synchronization on the oscilloscope and B synchronization on the picoscope.

### 3.0 Testing Procedure—Measurements through software

3.1 Picoscope Data Analysis

1. Before synchronizing, but with both generator B and the reference generator's on, hook up the probes to point 2 and point 4.
2. After pressing the green play button, two out-of-phase 60 Hz, 24Vpp waveforms should show up on the picoscope live feed.
3. After a few seconds, save the data to a CSV file (make note of the CSV file name).
4. After synchronization, repeat the previous step, creating another CSV file under a different name.
5. Then, go to MATLAB, make sure the CSV files are in the workspace path, and input the proper file names.
6. Run the script.
a. Two figures comparing the channel inputs for before synchronization and after synchronization should appear.
b. Figures showing the frequency response of the 4 waveforms (Channel 1 before and after synchronization and Channel 2 before and after synchronization) should appear showing the frequency of each waveform, which should be in the vicinity of 60 Hz.
c. The peak to peak voltage should be displayed.

3.2 Collecting data from the DAQ

Now we can add loads to the system.
1. Run MATLAB code to establish connection to the DAQ, read out available channels
a. Make sure sensor board wiring is correct
2. Connect the resistive load to any “Load 1” output from the transmission lines, through the sensor board, and make sur
a. Run the MATLAB script to collect data from the DAQ
b. The voltage and current signals will be displayed, as well as the frequencies of the load circuit
3. Switch out the resistive load with inductive load, repeat
4. Switch out inductive load with Citgo sign, repeat

### 4.0 Measurable Criteria

Success for this prototype testing will be measured by the following criteria:

1. Successfully start the grid with both generators synchronized and connected to the grid
a. Synchronization means the 2 generators are connected to the grid and no major changes in frequency and Vppp are observed. Note: synchronization does not mean all three generators will be in phase.
2. Successfully connect the picoscope to the grid, and observe the live feed, using it to synchronize generator B.
3. Successfully download a .CSV file from the picoscope and run the MATLAB script on the data collected.
a. The MATLAB script should output frequencies of 60 Hz +/- 10 Hz, and peak to peak voltages of 24 Vpp +/- 5V.
4. Successfully connect and collect data from the DAQ, understand what the data is showing about the loads inserted to the grid.

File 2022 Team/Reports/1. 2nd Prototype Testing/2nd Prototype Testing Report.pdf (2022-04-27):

To: | Professor Pisano
From: | Aidan, McCall, Jonas Escobar
Team: | Smart Grid (30)
Date: | 03/10/22

Subject: 2nd Prototype Testing

### 1.0 Materials Required

Hardware
- Smart Grid Test Facility
- DC Power Supply (3.3V, 5V)
- Oscilloscope
- Picoscope
- NI myDAQ
- Banana cables/BNC-Alligator probes

Software
- MATLAB
- MATLAB Signal Processing packages
- Proper daq driver softwares
- NI DAQmx Elvis/driver software
- MATLAB Data Acquisition Toolbox
- MATLAB Data Acquisition Toolbox Support Package for NI-DAQmx Devices
- Data collection scripts

### 2.0 Setup

2.1 Preparing the model for operation

1. Plug the power strip into the wall. Though the presence of a benchtop power supply is a
| current design flaw (we would like to find a solution for easier transport), we are still using it to power the control boards (MSP430s) for now.

## Senior Design

## ENG EC 463

2. Before connecting the model, the 6V output is set to 3.3V, and the +25V output is set to 5V, and both sides are grounded. With the output turned off, we wire the leads to the corresponding inputs on the outside of the model.
3. Turn on the oscilloscope and wire the leads to points 1 and 3, according to Figure 1.

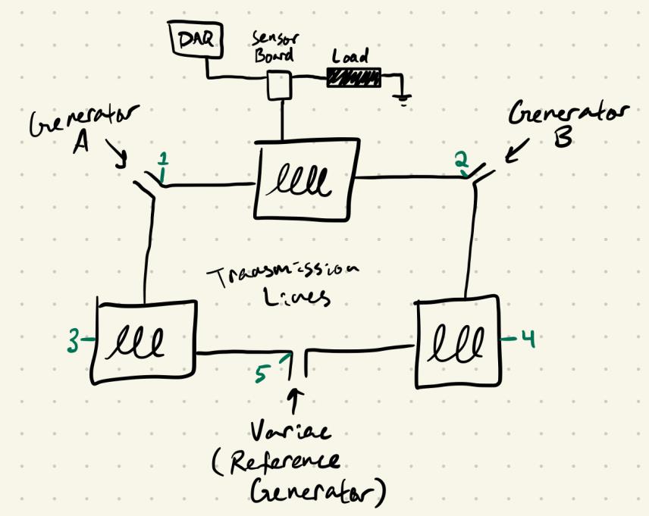
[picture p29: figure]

Figure 1: Basic schematic of the grid

4. All the hardware is set, so turn on the output of the benchtop power supply, in order to let the microcontrollers settle.
5. Then turn on the main switch on top, labeled 24V, to bring power to the rest of the model
6. The variac/reference generator is turned on after. The reference waveform should be visible on the oscilloscope (from point 3), at 60Hz and 24Vpp.

2.2 Setting up the Picoscope

1. Plug the picoscope into a computer.
2. Attach the probes to point 2 (Channel 1) and point 4 (Channel 2).
3. Pulling up the PicoScope 6 application should bring up a live feed with the 60 Hz, 24Vpp wave being visible on the computer.

2.3 Activating the generators and synchronizing

1. To turn on a generator, we reset the microcontroller by pressing the button labeled by an arrow for the MSP430 corresponding to that generator. When the button for A is pressed, the generator will begin its rotation and it should now be visible on the oscilloscope (from point 1). Their peak-to-peak voltage should be close to the same.
2. Next, flip the slide switch on the synchronization circuit for A to the green/on position, which will give additional feedback via the LED. The LED will flicker on and off due to the phase differences between the reference generator and the signal produced by generator A; the two signals are in phase when the LED is dim, and out of phase when it is lit up (i.e. out of phase means there will be a voltage difference across the diode causing it to be lit).
3. The toggle switch (with on/off labels) should be closed (switched to on) at a moment when the two waves are in phase.
4. Closing this will short circuit the two nodes we’re measuring on the oscilloscope, so the probe at point 3 should be moved to point 5 to compare generator A to the reference. This way we can check that the peak-to-peak voltage is remaining constant, and if it’s not then the main 24V switch should be switched off, along with the variac, to reset the model and start over. In theory, the frequency of generator A should also stabilize to 60Hz, but we’re not currently seeing this behavior.
5. These steps will be repeated for generator B, using the PicoScope to view the waveforms. After closing the toggle switch, generator B should then be compared to either generator A or the reference generator. If voltages are remaining constant, then the grid is running properly. We plan to measure A synchronization on the oscilloscope and B synchronization on the picoscope.

### 3.0 Detailed Measurements Taken

3.1 Picoscope Data Analysis

From the Picoscope, we observed live data (seen in Figure 2.) in order to synchronize the generator B to the reference. After saving a CSV. file to MATLAB. We ran a Matlab script, which outputs the data shown in Figure 3,4, and 5. This includes frequency response of the waveforms to assure the frequency is in the range of 60 Hz, the voltage waveform showing the waves synchronized and unsynchronized, and an output of Vpp for each waveform, which amounts to about 24 V (16.97 Vrms). These figures can be used to visually display the synchronization process, while outputting the frequency and voltage data that confirms the correct values.

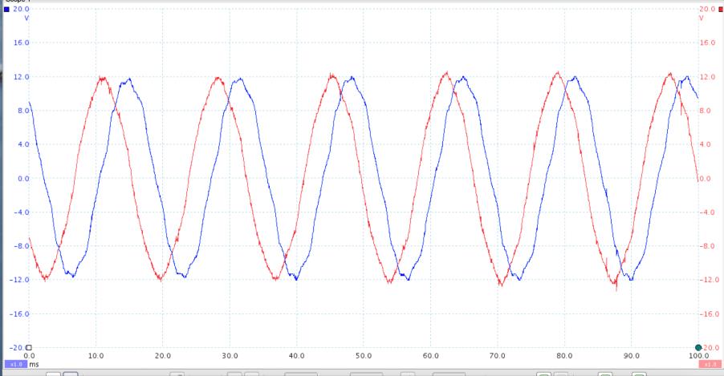
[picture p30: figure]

Figure 2: Live Data from the Picoscope with the probes attached to point 2 (Channel 1: blue) and point 4 (Channel 2: red) from Figure 1 as defined in the setup.

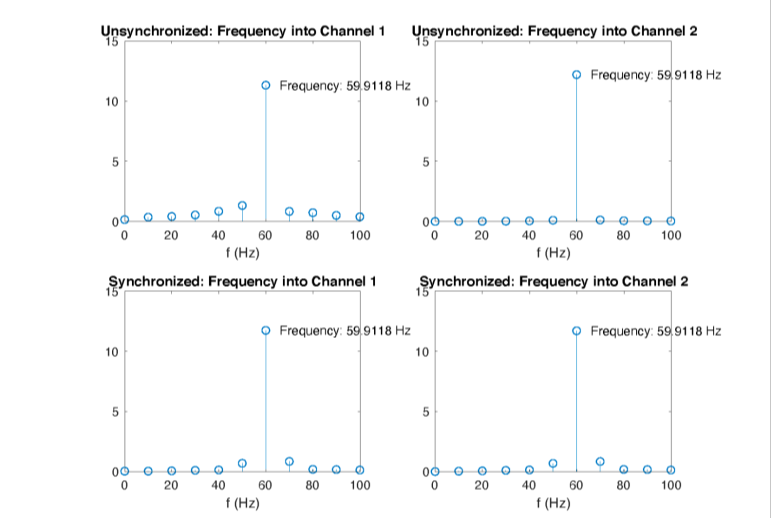
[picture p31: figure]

Figure 3: The frequency response for each channel's waveform before and after synchronization

Figure 4: The average peak-to-peak voltage before and after synchronization

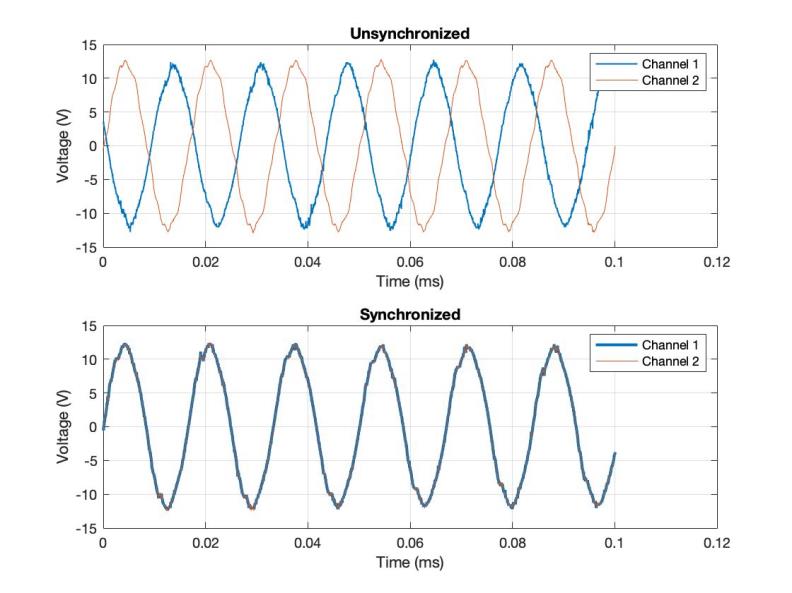
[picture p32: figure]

Figure 5: Data plotted which visually shows the two channels before and after synchronization.

3.2 Collecting data from the DAQ

Next, we added loads to the system. To test the DAQ, we ran the prepared MATLAB script, and saw how the data was different for each type of load. For the inductive load, the current and voltage are more out of phase than the resistive load, which makes sense for the phasers.

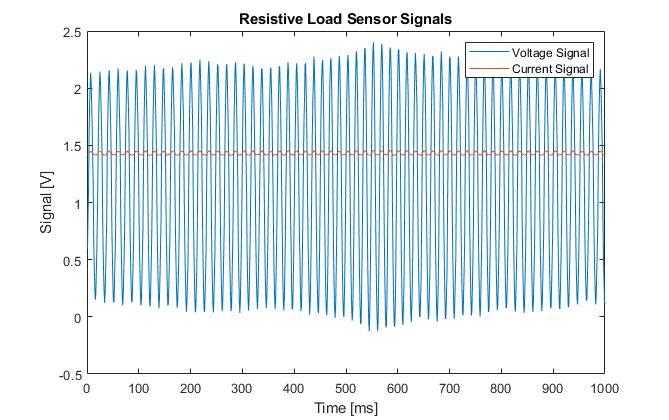
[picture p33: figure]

Figure 6: Waveform recorded by DAQ with “Load” of Figure 1 entirely resistive.

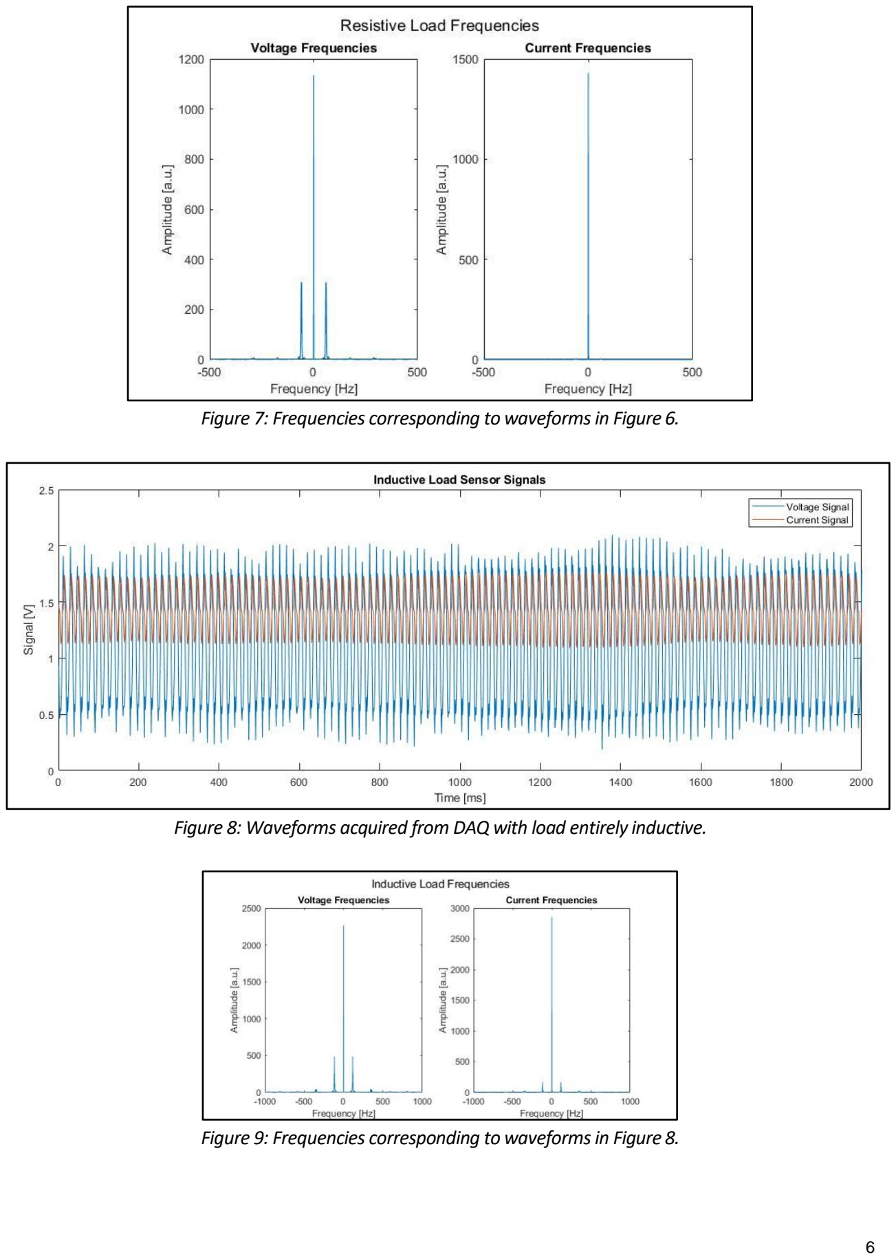
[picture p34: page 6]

Figure 7: Frequencies corresponding to waveforms in Figure 6.

Figure 8: Waveforms acquired from DAQ with load entirely inductive.

Figure 9: Frequencies corresponding to waveforms in Figure 8.

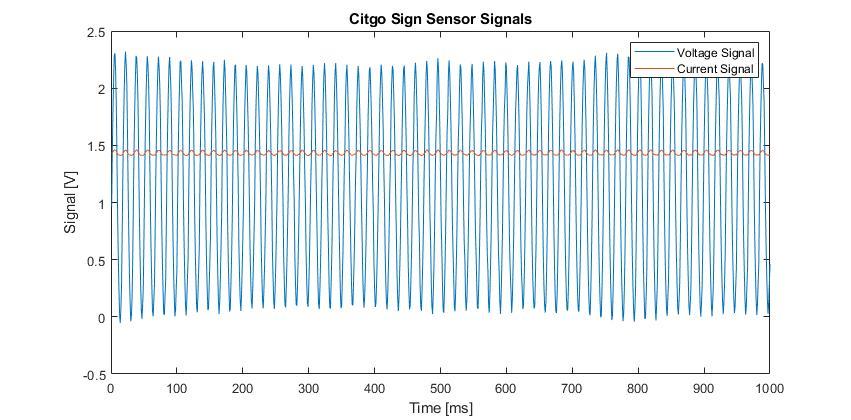
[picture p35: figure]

Figure 10: Waveforms acquired from DAQ with a scale Citgo Sign as the load. (Resistive with diodes).

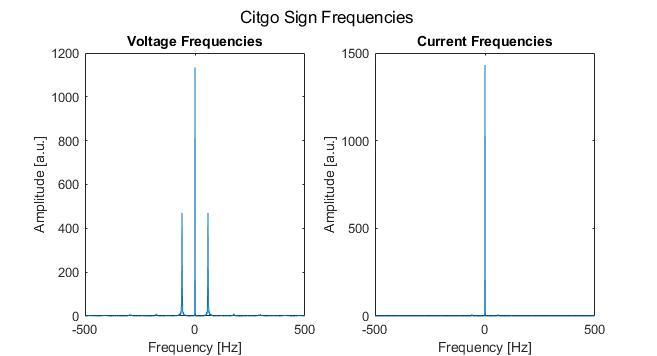
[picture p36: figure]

Figure 11: Frequencies corresponding to waveforms in Figure 10.

### 4.0 Conclusion

Success for this prototype testing was measured by the following criteria:

1. Successfully start the grid with both generators synchronized and connected to the grid
a. Synchronization means the 2 generators are connected to the grid and no major changes in frequency and Vpp are observed. Note: synchronization does not mean all three generators will be in phase.
2. Successfully connect the picoscope to the grid, and observe the live feed, using it to synchronize generator B.

3. Successfully download a .CSV file from the picoscope and run the MATLAB script on the data collected.
a. The MATLAB script should output frequencies of 60 Hz +/- 10 Hz, and peak to peak voltages of 24 Vpp +/- 5V.
4. Successfully connect and collect data from the DAQ, understand what the data is showing about the loads inserted to the grid.

All criteria were successfully met during prototype testing as seen in Section 3.0 of this report. Based on test data, the grid is working as expected. The grid is outputting a 24 Vpp, 60 Hz waveform and our instrumentation is properly collecting data. When the resistor is used as the load, we observe no phase shift between the load voltage and current. When the inductors are used, we observe a phase shift between the load voltage and current. Of course, we still have some improvements to make, including building the UI itself for control of the DAQ and data processing. This prototype testing was mainly to test the setup of the model and its operation, as well as the core instrumentation and basic data processing in MATLAB. While the picoscope data was not yet collected in MATLAB, our fundamental system is ready and we plan to bring all of these pieces together in a first draft of the UI, which we can then review with the client for suggestions on additional useful data points.

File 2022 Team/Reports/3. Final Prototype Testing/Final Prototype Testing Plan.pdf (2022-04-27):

# Final Prototype Test Plan

To: | Professor Pisano
From: | Aidan McCall, Jonas Escobar
Team: | Team 30: Smart Grid
Date: | 4/7/22

Subject: Final Prototype Test Plan

### 1.0 Materials Required

Hardware
- Smart Grid Test Facility
- PC Computer
- PicoScope
- NI myDAQ
- Banana cables/BNC-Alligator probes
- Electrical outlet

Software
- MATLAB
- MATLAB Signal Processing packages
- Proper DAQ driver softwares
- NI DAQmx Elvis/driver software
- MATLAB Data Acquisition Toolbox
- MATLAB Data Acquisition Toolbox Support Package for NI-DAQmx Devices
- Final GUI
- Picoscope App
- PicoScope analysis MATLAB script

## Senior Design

## ENG EC 464

### 2.0 Setup

2.1 Preparing the model for operation

1. Plug the power strip into the wall. This powers the variac (which starts in the OFF position),
| the +/- 15 V power supply that powers the sensor boards, the 24 VDC power supply that powers the generators.
2. Make sure that all transmission lines have the top three switches ON and the bottom three
| switches OFF.
3. Before connecting the model, plug in the 5V 1A power adapter that powers the
| synchronization circuits. Once plugged in, the LEDs on the MSP30's should light up.
4. Wait a few seconds to let the MSP30's settle, and then turn on the main switch on top, labeled
| 24V, to bring power to the rest of the model.
5. The variac/reference generator is turned on after.

2.2 Setting up the PicoScope

1. Plug the PicoScope into a computer.
2. Attach the probes to point 1 and point 3 (comparing Generator A to the point it is being added
| to the grid), according to Figure 1.

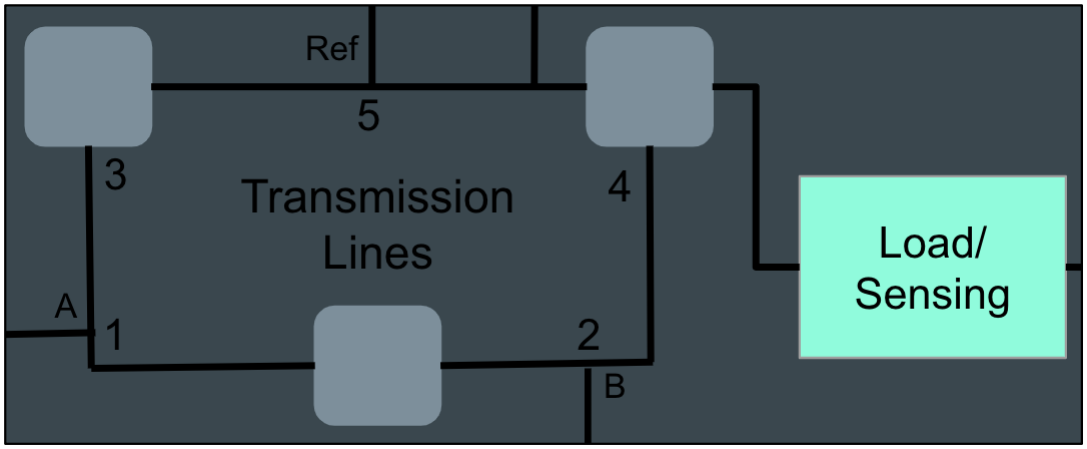
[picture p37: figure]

Figure 1: Basic schematic of the grid

3. Pulling up the PicoScope 6 application should bring up a live feed with the 60 Hz, 24Vpp wave being visible on the computer, which is coming from the reference variac.

2.3 Activating the generators and synchronizing

1. To turn on a generator, we reset the microcontroller by pressing the button labeled by an arrow for the MSP430 corresponding to that generator. When the button for A is pressed, the generator will begin its rotation and it should now be visible on the PicoScope (from point 1). The peak-to-peak voltage should be about the same as the reference.
2. Next, flip the slide switch on the synchronization circuit for A to the green/on position, which will give additional feedback via the LED. The LED will flicker on and off due to the phase differences between the reference generator voltage and the signal produced by generator A; the two signals are in phase when the LED is dim, and out of phase when it is lit up (i.e. out of phase means there will be a voltage difference across the diode causing it to be lit).
3. The toggle switch (with on/off labels) should be closed (switched to on) at a moment when the two waves are in phase.
4. Closing this will short circuit the two nodes we’re measuring on the PicoScope, so the probe at point 1 should be moved to point 5 to compare generator A to the reference. This way we can check that the peak-to-peak voltage is remaining constant, and if it’s not then the main 24V switch should be switched off, along with the variac, to reset the model and start over. The frequency of generator A should also stabilize to the reference 60Hz, but there may be some instability.
5. These steps will be repeated for generator B, with the PicoScope initially measuring at points 2 and 4 in Figure 1 (moving point 2 to point 5 in step 4). After closing the toggle switch, if voltage amplitudes are remaining constant, then the grid is running properly.

### 3.0 Testing Procedure—Measurements through Software

3.1 PicoScope/waveform visualization

1. Before synchronizing, but with both generator B and the reference generator's on, hook up the probes to point 2 and point 4.
2. After pressing the green play button, two out-of-phase 60 Hz, 24Vpp waveforms should show up on the PicoScope live feed.
3. Two waveforms for each channel input will be visible in the same time domain, allowing a visual comparison of the phase properties at different points on the grid.

3.2 Collecting data from the DAQ

1. Before plugging in any loads, run MATLAB GUI and press “Connect DAQ” to establish connection to the DAQ. This will set up two channels to collect current and voltage.
a. The DAQ should be connected to the sensor board at this time.
2. Once connection is established, plug the inductive load into the sensor board. And connect the sensor board to the grid. The inductive load is not being powered by the grid.


Figure 2: This schematic shows how the load is connected with the grid. The R, L, and C values are attached to the transmission lines.


Figure 3: This schematic shows how the load is connected when making the assumption that the two voltage sources are phase locked.

3. Press the "Record DAQ" button, which should bring up two waveforms for current and voltage that are approximately sinusoidal.
4. Press the "Phasor Calculation" Button, and the phase, power factor, RMS voltage, and RMS current should appear.

5. Repeat Steps 3 and 4 for various inductor measurements; different arrangements of the inductor PCB switches are outlined in Table 1.
6. Turn the generator input switches to OFF to remove the generators from the grid, leaving the reference switch ON, so that only the reference generator is powering the grid.
7. Repeat Steps 3-5. Compare these measurements to the calculated values in Table 1.

Table 1:

Switch Configuration | Load (H) | Calculated Phase (degrees)
S1, S8 | 0.1901 | -81.852064
S1, S2, S3, S4, S5, S8 | 0.144 | -79.450134
S1, S4, S6, S8 | 0.1301 | -78.425619
S1, S2, S4, S5, S6, S8 | 0.1028 | -75.713664
S1, S4, S7, S8 | 0.0821 | -72.659963

### 4.0 Measurable Criteria

Success for this prototype testing will be measured by the following criteria:

1. Successfully operate the grid entirely on-cart.
2. Successfully start the grid with both generators synchronized and connected to the grid
a. Synchronization means the 2 generators are added to the grid and no major changes in frequency and Vpp are observed. Note: all three generators will not necessarily be in phase.
3. Successfully connect the PicoScope to the grid, and observe the live feed, using it to synchronize generator B.
4. Successfully connect and collect data from the DAQ, understand what the data is showing about the loads inserted to the grid.
5. Successfully plot voltage, current, and phase data for an inductive load.
a. Plots should be sinusoidal. Current should lag voltage.
6. When the reference generator is the only power supply, the measured angles should be within 7°

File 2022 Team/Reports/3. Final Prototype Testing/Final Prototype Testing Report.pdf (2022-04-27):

# Final Prototype Test Report

To: | Professor Pisano
From: | Aidan McCall, Jonas Escobar
Team: | Team 30: Smart Grid
Date: | 4/8/22

Subject: Final Prototype Test Plan

### 1.0 Materials Required

Hardware
- Smart Grid Test Facility
- PC Computer
- PicoScope
- NI myDAQ
- Banana cables/BNC-Alligator probes
- Electrical outlet

Software
- MATLAB
- MATLAB Signal Processing packages
- Proper DAQ driver softwares
- NI DAQmx Elvis/driver software
- MATLAB Data Acquisition Toolbox
- MATLAB Data Acquisition Toolbox Support Package for NI-DAQmx Devices
- Final GUI
- Picoscope App
- PicoScope analysis MATLAB script

## Senior Design

## ENG EC 464

### 2.0 Setup

2.1 Preparing the model for operation

1. Plug the power strip into the wall. This powers the variac (which starts in the OFF position),
| the +/- 15 V power supply that powers the sensor boards, the 24 VDC power supply that powers the generators.
2. Make sure that all transmission lines have the top three switches ON and the bottom three
| switches OFF.
3. Before connecting the model, plug in the 5V 1A power adapter that powers the
| synchronization circuits. Once plugged in, the LEDs on the MSP30's should light up.
4. Wait a few seconds to let the MSP30's settle, and then turn on the main switch on top, labeled
| 24V, to bring power to the rest of the model.
5. The variac/reference generator is turned on after.

2.2 Setting up the PicoScope

1. Plug the PicoScope into a computer.
2. Attach the probes to point 1 and point 3 (comparing Generator A to the point it is being added
| to the grid), according to Figure 1.


Figure 1: Basic schematic of the grid

3. Pulling up the PicoScope 6 application should bring up a live feed with the 60 Hz, 24Vpp wave being visible on the computer, which is coming from the reference variac.

2.3 Activating the generators and synchronizing

1. To turn on a generator, we reset the microcontroller by pressing the button labeled by an arrow for the MSP430 corresponding to that generator. When the button for A is pressed, the generator will begin its rotation and it should now be visible on the PicoScope (from point 1). The peak-to-peak voltage should be about the same as the reference.
2. Next, flip the slide switch on the synchronization circuit for A to the green/on position, which will give additional feedback via the LED. The LED will flicker on and off due to the phase differences between the reference generator voltage and the signal produced by generator A; the two signals are in phase when the LED is dim, and out of phase when it is lit up (i.e. out of phase means there will be a voltage difference across the diode causing it to be lit).
3. The toggle switch (with on/off labels) should be closed (switched to on) at a moment when the two waves are in phase.
4. Closing this will short circuit the two nodes we’re measuring on the PicoScope, so the probe at point 1 should be moved to point 5 to compare generator A to the reference. This way we can check that the peak-to-peak voltage is remaining constant, and if it’s not then the main 24V switch should be switched off, along with the variac, to reset the model and start over. The frequency of generator A should also stabilize to the reference 60Hz, but there may be some instability.
5. These steps will be repeated for generator B, with the PicoScope initially measuring at points 2 and 4 in Figure 1 (moving point 2 to point 5 in step 4). After closing the toggle switch, if voltage amplitudes are remaining constant, then the grid is running properly.

### 3.0 Testing Procedure—Measurements through Software

3.1 Current and Voltage Waveforms

After setup was complete, the PicoScope and DAQ were connected to the computer for collecting data. To view the sources for the load under test, we placed the two oscilloscope channels on either side of the transmission line PCB that the load was added to. Before the load is added, the grid signal is a clean sine wave, but Figure 2b shows how the addition of the load changes the quality of that sine wave. While both generators are on, this wave fluctuates in both amplitude and frequency. Additionally, the theoretical phase angle is different from what we calculate from the measurement (Figure 2a shows the measurement result). However, when the generators are removed from the grid, and only the reference generator is powering the load (Figure 3), the measured phase matches the theoretical phase within 5°. The source signal (3b) also has less fluctuation, but the sine wave is highly distorted by harmonics.


Figure 2 & 3: Current and voltage signals, phase diagram, and calculated values measured in the inductive load circuit are shown in the left GUI window (2a, 3a). The right window (2b, 3b) shows the oscilloscope signal measured at points 1 and 2 in Figure 1; in Figure 3, generators A and B were removed from the grid.

3.2 Phase Angle Measurements Taken

Two different angles were measured for a certain switch configuration. One angle was measured when Generator A and B were connected to the grid. The second angle was measured when only the reference generator was generated. Table 1 shows the results of the testing.

Table 1

Load (H) | Calculated Phase (degrees) | Measured Phase (degrees) with only Reference Generator | Measured Phase (degrees) with Gen A, B, and Reference
0.1901 | -81.852064 | -83.04 | -47.89
0.144 | -79.450134 | -75.65 | -33.76
0.1301 | -78.425619 | -77.71 | -36.68
0.1028 | -75.713664 | -71.22 | -29.21
0.0821 | -72.659963 | -74.15 | -33.13

### 4.0 Success Criteria

Success for this prototype testing was measured by the following criteria:

1. Successfully operate the grid entirely on-cart.
2. Successfully start the grid with both generators synchronized and connected to the grid
a. Synchronization means the 2 generators are added to the grid and no major changes in frequency and Vpp are observed. Note: all three generators will not necessarily be in phase.
3. Successfully connect the PicoScope to the grid, and observe the live feed, using it to synchronize generator B.
4. Successfully connect and collect data from the DAQ, understand what the data is showing about the loads inserted to the grid.
5. Successfully plot voltage, current, and phase data for an inductive load.
a. Plots should be sinusoidal. Current should lag voltage.
6. When the reference generator is the only power supply, the measured angles should be within 7°

### 5.0 Conclusions

Based on these measurements, this prototype test was a success under the measurable criteria stated above.

1. The grid was successfully operated entirely on-cart.
2. The generators were successfully synchronized and connected to the grid.
3. The PicoScope was successfully used to synchronize while observing the live feed.
4. We successfully connected to the DAQ and collected data.
5. We successfully plotted voltage, current, and phase data for an inductive load.

a. The phasor diagram was accurate and visually useful for potential use in a classroom setting.
b. The voltage and current data appeared to have harmonics as seen in Figure 3. Based on the data and testing different points in the grid, it appears that the issue is likely with the sensor boards or the inductive load itself. Because the inductive loads are hand-wound and close together, this could be causing issues and distorting the signal. To combat this, we are going to try to test the sensor board with different loads to see if that is the issue. If it is not, we will make new inductive loads with a breadboard to try to get a more clear signal.
6. Based on Table 1, the measured data was all within 7° of the calculated data when only the reference generator was connected. Ideally, when the issue with the harmonics is fixed, the measured data should always be correct regardless of which generators are connected. However, because we measured the correct data with the reference generator, it can still be used as a helpful tool to use in class.

Before ECE Day, we would like to clean up some of the data measurements. Nevertheless, our GUI is working as expected.

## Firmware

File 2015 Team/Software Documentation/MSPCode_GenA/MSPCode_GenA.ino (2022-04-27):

// Rotary Encoder Code
// Marissa Petersile & Tim Leung
// BU ECE Team 14, Class of 2015

// Manually included by Energia
// #include Energia.h if necessary

// Define direction register, output register, and select registers
    #define TA_DIR P1DIR
    #define TA_OUT P1OUT
    #define TA_SEL P1SEL

// Define the bit mask (within the port) corresponding to output TA1
    #define TA1_BIT 0x04

// MAIN FUNCTION ---------------------------------------------
int main(){
  
    WDTCTL = WDTPW + WDTHOLD; // Stop/withhold watchdog timer
    BCSCTL1 = CALBC1_16MHZ; // 8MHz calibration for clock
    DCOCTL = CALDCO_16MHZ;
 
//SETUP THE TIMER (ONCE ONLY) ---------------------------------
    TACTL = TACLR; // reset clock
    TACTL = TASSEL_2+ID_0; // clock source = SMCLK
    // clock divider = 8
    // (clock still off)
    TACCTL0=0; // Nothing on CCR0
    TACCTL1=OUTMOD_7; // reset/set mode
    TACCR0 = 850; // period-1 in CCR0 //18.7kHz
    TACCR1 = 570; // duty cycle in CCR1, change this during loop
    TA_SEL|=TA1_BIT; // connect timer 1 output to pin 2
    TA_DIR|=TA1_BIT;
    TACTL |= MC_1; // timer on in up mode

// DECLARE VARIABLES AND CONSTANTS -----------------------------
    // Measurement Variables
    double diff;
    unsigned long pulseHI;
    long int perIN;
    int duty;
    double perALT;
    
    // Button 1: Each Press makes +0.2Hz
    const int buttonPin1 = 7;
    int buttonState1 = 0;
    pinMode(buttonPin1, INPUT);
    int counterButton1 = 0;
    int dbval1 = 1;
    int debounce1 = true;
    double checkPER;
    
    //Button 2: Each Press makes -0.2Hz
    const int buttonPin2 = 15;
    int buttonState2 = 0;
    pinMode(buttonPin2, INPUT);
    int counterButton2 = 0;
    int dbval2 = 1;
    int debounce2 = true;

    // Fixed values and initialize clock
    int dutyCNG = 1;
    unsigned int counter = 1;
    duty = 570; // 67% duty cycle makes 60Hz
    double perDES = 16666.666; // in us
    int wait = 5000000; // wait 5s before giving up on signal

      

// SAMPLING LOOP: DUTY CYCLE ADAPTER ----------------------------
    while(true)
    {
       counter++;
    
       if (counter % 20000 == 0)
       {
           // Measure period of input signal (us)
           pulseHI = pulseIn(P1_4, HIGH, wait);
           perIN = 2*pulseHI;
           
           
      //Check if Button 1 is being pressed (-0.2Hz)
      buttonState1 = digitalRead(buttonPin1);
      if (buttonState1 == HIGH)
        {
          // Debounce the reading to ensure each HIGH is one button press
          if (debounce1)
            {
              counterButton1++;
              if (counterButton1 >= dbval1)
                {   
                  debounce1 = false;
                  
                  // Make sure new perDES is between 50Hz and 70Hz
                  checkPER = perDES + 55.4;
                  if (checkPER >= 20000)
                      perDES = 20000; // min at 50 Hz
                  else
                      perDES += 55.4; // Equivalent to 0.2Hz change
                }
            }
            
          else
            {
              counterButton1 = 0;
            }
        }
    
      // If not in debounce mode, reset conditions  
      else 
        {
          counterButton1 = 0;
          debounce1 = true;
        }
        

      //Check if Button 2 is being pressed (+0.2Hz)
      buttonState2 = digitalRead(buttonPin2);
      if (buttonState2 == HIGH)
        {
          if (debounce2)
            {
              counterButton2++;
              if (counterButton2 >= dbval2)
                {   
                  debounce2 = false;
                      
                  // Make sure new perDES is between 50Hz and 70Hz
                  checkPER = perDES - 55.4;
                  if (checkPER <= 14286)
                      perDES = 14286; // max at 70Hz
                  else
                      perDES -= 55.4; // Equivalent to 0.2Hz change
                }
            }
          else
            {
              counterButton2 = 0;
            }
        }
      
      // If not in debounce mode, reset conditions 
      else 
        {
          counterButton2=0;
          debounce2 = true;
        }
        
           // Adapt from encoder frequency to alternator frequency
           perALT = perIN*25.75; // constant known from measurement
           
           // Calculate deviation from 60Hz
           diff = perALT - perDES; // change in period in us
              
           // CASE 1: freqIN = freqDES or is very close 
           if (abs(diff) == 0) 
           {
             // Do nothing
           }
  
  
           // CASE 2: freqIN > freqDES; need duty cycle to decrease
           else if (diff < 0)
           {
  
               // Small Change
               if (abs(diff) <= 800)
               {
                  duty -= dutyCNG*10;
               } 
         
               // Medium Change
               else if (abs(diff) <= 1000)
               {
                  duty -= dutyCNG*20;
               } 
           
               // Large Change
               else if (abs(diff) <= 1500)
               {
                  duty -= dutyCNG*30;
               } 
               
               // Max Change
               else
               {
                  duty -= dutyCNG*50;
               }  
            } 
  
            // CASE 3: freqIN < freqDES, need duty cycle to increase
            else if (diff > 0)
            {

               // Small Change
               if (diff <= 800)
               {
                  duty += dutyCNG*10;
               } 
             
               // Medium Change
               else if (diff <= 1000)
               {
                  duty += dutyCNG*20;
               } 
               
               // Large Change
               else if (diff <= 1500)
               {
                  duty += dutyCNG*30;
               } 
               
               // Max Change
               else
               {
                  duty += dutyCNG*50;
               } 
              
             }
  
  // Keep duty cycle from saturating or becoming DC
  if (duty >= 850)
  {
      duty = 850;
  }
  
  else if (duty <= 1)
  {
      duty = 1;
  }
  
  
  // Update duty cycle on output signal
  TACCR1 = duty;
  
  // Reset clock
  counter = 1;
 
    } // end timer-based loop
  
    } // end always-true loop

  
  // Stop CPU and enable interrupts (never occurs if progream does not break)
  __bis_SR_register(GIE+LPM0_bits);

 
  return 0;
}

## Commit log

2022-04-27 Previous Work Upload
    [5Vregulator.PcbLib, ACMount.SLDPRT, ACPulley.SLDPRT, ACS712.SchLib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]
2022-04-29 Final Upload
    [Bill of Materials.xlsx]
